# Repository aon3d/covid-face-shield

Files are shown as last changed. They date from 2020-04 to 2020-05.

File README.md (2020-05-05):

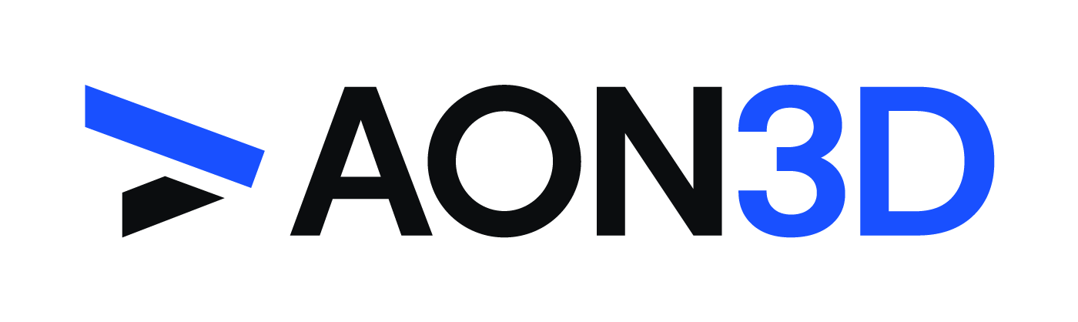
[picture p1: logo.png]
AON3D Logo (https://www.aon3d.com/)


# COVID-19 Face Shield

> [Need 3D Printed Medical Supplies to Fight COVID-19?](https://www.aon3d.com/3d-printed-medical-supplies-to-fight-covid-19/)

TL;DR: [Here is what the model looks like](models/COVID-001-Face-Shield-Frame-R01.STL).

The government of Canada has [recently come out with guidance](https://www.canada.ca/en/health-canada/services/drugs-health-products/medical-devices/covid-19-unconventional-manufacturing-personal-protective-equipment.html) regarding unconventional manufacturing of personal protective equipment in response to COVID-19.
As there are already many sites, forums, and social media efforts organizing people with access to 3D printers to support their local healthcare workers, we wanted to help standardize the design efforts.

To avoid medical professionals and our front line workers from having to adapt to a multitude of designs from different sources, we hope that grassroots efforts adopt a common design to minimize chances of a negative user experience.
As such, we are publishing our design, assembly instructions, MSDS, QC checklist, and all other documentation to help jumpstart others who want to get involved and help.

## How are we helping?

We are working with local health authorities in Montréal to produce desperately needed medical supplies and protective equipment.
Specifically, we are fabricating face shield to help protect our front line workers from splash and debris.

Our design and manufacturing methodology focuses on fulfilling short-term needs using additive manufacturing (e.g., 3D printing) to act as a stopgap while organizing medium-volume manufacturing (e.g., laser cutting, die cutting).
This two-step approach leverages our expertise (additive manufacturing) as well as a robust and local supply chain.
In this way, urgent needs due to shortages can be successfully satisfied while large-volume manufacturing (e.g., molding) catches up.
As such, the chosen face shield design is optimized for both laser cutting and 3D printing.

<p>
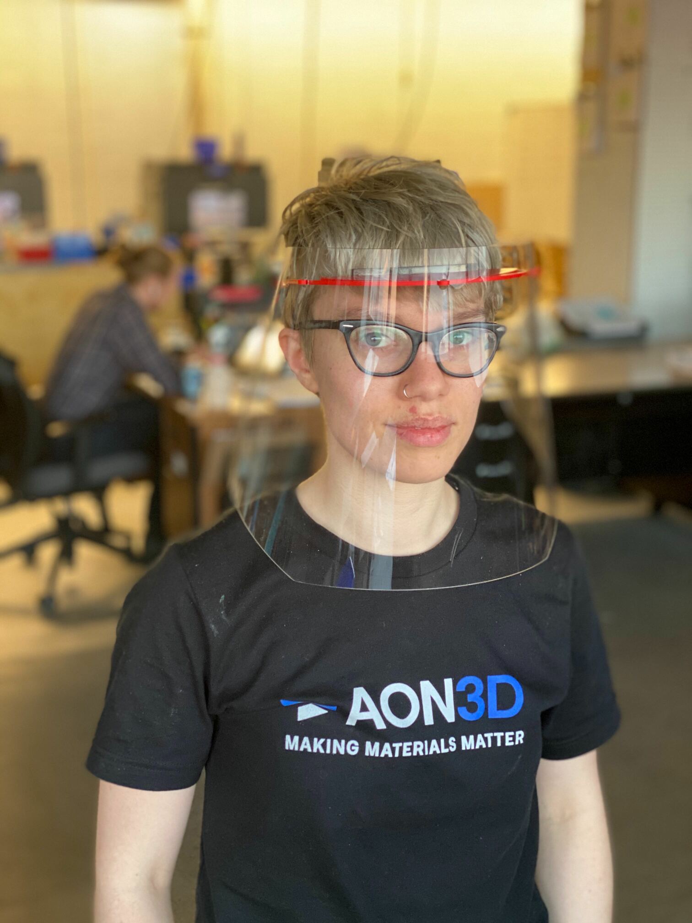
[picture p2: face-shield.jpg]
Face shield.

</p>

## Contents

- [COVID-19 Face Shield](#covid-19-face-shield)
  - [How are we helping?](#how-are-we-helping)
  - [Contents](#contents)
  - [Face Shield Design](#face-shield-design)
    - [Requirements and Specifications](#requirements-and-specifications)
      - [Visor](#visor)
      - [Frame](#frame)
    - [Bill of Materials](#bill-of-materials)
    - [Handling](#handling)
    - [Packaging](#packaging)
      - [Bag A (6” poly tubing)](#bag-a-6-poly-tubing)
      - [Bag B (12” poly tubing)](#bag-b-12-poly-tubing)
      - [Bag C (12” poly tubing)](#bag-c-12-poly-tubing)
      - [Box](#box)
  - [Design Files](#design-files)
  - [Documentation](#documentation)
  - [Printing Instructions](#printing-instructions)
    - [Printer Preparation](#printer-preparation)
    - [Frame Printing](#frame-printing)
    - [Frame Removal](#frame-removal)
  - [Development](#development)
    - [PDF Generation](#pdf-generation)
      - [Requirements](#requirements)
      - [Procedure](#procedure)
    - [Releases](#releases)
  - [Disclaimer](#disclaimer)

## Face Shield Design

Our face shield design is based on the [open-source work published by Georgia Tech](https://pwp.gatech.edu/rapid-response/face-shields/).
While the design is nearly identical, we have made the following modifications:

- Visor
  - Diameter of snap-on holes increased from 6.35mm to 7mm for an easier fit
- Frame
  - -0.25mm horizontal compensation
  - Thickness of 1/8" (3.175mm)
  - A [second iteration of the frame](models/COVID-001-Face-Shield-Frame_CNC_1_8-R01.STEP) is available and accommodates CNC milling with a 1/8" cutter

These modifications were done to better support our specialty, additive manufacturing, while also being compatible with future medium volume production methods, such as laser cutting and CNC milling.

### Requirements and Specifications

#### Visor

- Must provide adequate coverage (CSA Z94.3 Sections 10.2.1/10.2.2/10.3/10.4)
- Should made of optically clear, distortion free, lightweight materials (CSA Standard Z94.3.1-16)
- Should be free of visible defects or flaws that would impede vision (ANSI Z87.1 Section 9.4)
- Should allow adequate space between the wearer’s face and the inner surface of the visor to allow for the use of ancillary equipment (medical/surgical mask, respirator, eyewear, etc.)
- Device should withstand impact from sharp or fast projectiles (ANSI Z87.1 Section 9.2 and 9.3, CSA Z94.3 Section 10.1)
- Material: PC, PETG, PET, Acetal, POM, Polypropylene, or PVC
- Thickness: 0.01” - 0.03”

#### Frame

- Device should fit snugly to afford a good seal to the forehead area and to prevent slippage of the device
- User contacting materials should provide adequate material biocompatibility (skin sensitivity and cytotoxic testing) (ISO 10993-5, 10)
- Must resist isopropyl alcohol (IPA)
- Material: PC, ABS, or Acetal
- Thickness: 1/8" or 3/16"

### Bill of Materials

| Item | Qty | Comments |
|---|---|---|
| Frame | 1 | Laser cut or 3D printed |
| Visor | 1 | Laser or die cut |
| Elastic | 4+ | Size 33 (e.g., McMaster-Carr `12205T78`) |

### Handling

As it seems a person can carry the virus and be asymptomatic, it is best to act as if you may be contagious and take precautions to avoid contaminating the face shield during production.

- Wash your hands before entering the manufacturing area
- Wash your hands before removing prints
- Wipe down tools with IPA before using them to remove prints
- Wear a mask while handling prints
- Do not enter the manufacturing area unless you are the designated operator on shift
- Prints are immediately bagged after removal from the machine

### Packaging

To make the user experience as simple as possible for front line workers, the following packaging procedure is recommended:

#### Bag A (6” poly tubing)

- 40x elastics

#### Bag B (12” poly tubing)

- 10x frames

#### Bag C (12” poly tubing)

- 10x face shield kits
  - Bag A
  - Bag B
  - 10x visors
  - Assembly instructions

#### Box

 - MSDS
 - 10x Bag C

## Design Files

All design files may be found in the [models](models/) folder.

- `DXF` files are for laser cutting
- `STL` files are for 3D printing
- `SLDPRT` and `STEP` files are for 3D CAD software (e.g., Solidworks, Inventor, Fusion 360)
- `factory` files are for [Simplify3D](https://www.simplify3d.com/) and are designed to work for the [AON-M2 industrial 3D printer](https://www.aon3d.com/aon-m2-2020-industrial-3d-printer/)

## Documentation

All documentation files may be found in the [docs](docs/) folder.
PDFs of the documentation may be found [here](https://github.com/aon3d/covid-face-shield/releases/latest).

- Material Safety Data Sheets ([English](docs/msds-en.md), [French](docs/msds-fr.md) and [Spanish](docs/msds-es.md)) are available
- [Assembly instructions](docs/assembly.md)

## Printing Instructions

The following instructions are intended for printing using the AON-M2 or AON-M2 2020.

### Printer Preparation

1. Install a 0.6 mm nozzle heater block assembly. Instructions [here](https://docs.aon3d.com/maintenance/replace_hba/).
2. Install the aluminum build plate. Ensure that the Kapton tape is in good condition on all the surfaces. (If not, follow [this procedure](https://docs.aon3d.com/maintenance/kapton_application/) to replace it.
3. Clean the surface with IPA (isopropyl alcohol), minimum concentration of 70% for disinfection purposes.
4. Apply an adhesive to the build platform to ensure ABS adhesion. Dimafix or hairspray are tested adhesives for ABS.
4. Load ABS in the 0.6 mm toolhead you want to use. Instructions [here](https://docs.aon3d.com/operation/material_switch/).
5. Preheat the machine to the following temperatures:

| Component  | Temperature |
|:----------:|:-----------:|
| Build platform  | 105°C  |
| Chamber    | 60°C        |

6. Once the chamber has reached thermal equilibrium, initiate the probing sequence on the entire bed  and set the Z offset. Instructions [here](https://docs.aon3d.com/calibration/z_calibration/).

Use these probe bounds:

| Parameter  | Value |
|:----------:|:-----:|
| Left       | 15    |
| Right      | 435   |
| X Count    | 10    |
| Front      | 15    |
| Back/Rear  | 435   |
| Y Count    | 10    |

### Frame Printing

We have included two generated G-code files that are ready for use on the AON-M2 and AON-M2-2020.
They are intended for use with ABS and a 0.6 mm nozzle.
One G-code file is specific for printing with T0 (left toolhead) and the other is for use with T1 (right toolhead).

If you wish to modify the files, the original factory files for use with Simplify 3D have been included.
However, the specified settings have been tested and any modification may cause print defects.

Each print will yield 5 face shield frames.

Plan 112g of ABS filament and just over 2 hours of print time per print.

### Frame Removal

How to remove the part from the build platform. Proceed following the aformentioned [handling](#handling) guidelines.

**The parts and machines are hot!**
- At the end of the print, the toolheads will move to the back of the machine for easy access to the printed frames.
- The build platform and the chamber will remain heated to allow for a quick restart.
- Remove the skirt (single outline of material).
- With the scraper, carefully detach the extremity of the face shield frame. This will initiate the rest of the removal. Gently detach the part by placing the scraper under the part.
- Place the parts in a sanitized bag for storage.

## Development

### PDF Generation

#### Requirements

- [`pandoc`](https://pandoc.org/)
- `make`
- [`ghostscript`](https://www.ghostscript.com/)
- `texlive`

#### Procedure

To generate all PDFs:

```bash
make pdf
```

### Releases

- This repo uses [Calendar Versioning (`CalVer`)](https://calver.org/overview.html), with the following format: `YYYY.MM.DD`
- Generated PDFs should be attached to the [GitHub release](https://github.com/aon3d/covid-face-shield/releases/latest)

## Disclaimer

Please see [`DISCLAIMER.md`](DISCLAIMER.md).

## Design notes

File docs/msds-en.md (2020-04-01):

---
title: Material Safety Data Sheet
logo: logo.png
titlepage: true
---

# Identification

| | |
|---|---|
| Product Name | Face Shield |
| Product Code | COVID-FACE-SHIELD |
| Use(s) | Face protection from splash and other debris |
| Company Name | Made in 3D Canada Inc. (dba AON3D) |
| Telephone | \+1 833-772-6633 |

# Hazard Identification

| | |
|---|---|
| Potential Hazard | Combustible |
| Other Comments | N/A |

# Composition/Information on Ingredients

| Component | Material(s) |
|---|---|
| Frame | ABS, HIPS, or Acrylic |
| Visor | Polycarbonate, PETG, PET, Acetal, PVC, or Polypropylene |
| Strap | Polyester, Rubber, Polypropylene, and/or Nylon |
| Buckle | Plastic |

# First-aid Measures

| | |
|---|---|
| Inhalation (breathing) | In case of inhalation of smoke or burnt, consult physician. |

# Fire-fighting Measures

| | |
|---|---|
| Flashpoint | N/A |
| Flammable class | Burnable |
| Extinguishing media | Class A fire extinguisher |
| General hazard | Evacuate personal downwind of fire to avoid inhalation of irritation or harmful fumes and smoke. |
| Hazardous combustion products | Harmful gases |

# Accidental Release Measures

Collect and treat according to local plastics waste procedures.

# Handling and Storage

| | |
|---|---|
| Handling & Storage | Keep away from flammable substances and ignition sources, and store in cool and dry condition. |

# Exposure Controls/Personal Protection

| | |
|---|---|
| Breath protection | Not required |
| Skin protection | Not required |
| Ventilation | Not required |

# Physical and Chemical Properties

| | |
|---|---|
| Appearance | Colour varies |

# Stability and Reactivity

| | |
|---|---|
| Chemical Stability | Stable under normal room conditions of temperature and pressure. |
| Incompatible products | None |
| Hazardous decomposition product | N/A |

# Toxicological Information

| | |
|---|---|
| Toxicity | The product is non-toxic. |
| Eye/skin/sensitization effect | This product is not expected to cause significant irritation. |

# Ecological Information

Not biodegradable.

# Disposal Considerations

Treat according to the local plastics waste procedures.

# Transport Information

Not regulated or restricted.

# Regulatory Information

## Minimum Specifications in Urgent Manufacturing Scenarios

- Device must provide adequate coverage (CSA Z94.3 Sections 10.2.1/10.2.2/10.3/10.4).
- Device should made of optically clear, distortion free, lightweight materials (CSA Standard Z94.3.1-16)
- Device should be free of visible defects or flaws that would impede vision (ANSI Z87.1 Section 9.4)
- The device should allow adequate space between the wearer’s face and the inner surface of the visor to allow for the use of ancillary equipment (medical/surgical mask, respirator, eyewear, etc.)
- Device should fit snugly to afford a good seal to the forehead area and to prevent slippage of the device
- Device should withstand impact from sharp or fast projectiles (ANSI Z87.1 Section 9.2 and 9.3, CSA Z94.3 Section 10.1)
- If available, device should display anti-fog behavior on inside and outside of shield. (CSA Standard Z94.3.1-16)
- User contacting materials should provide adequate material biocompatibility (skin sensitivity and cytotoxic testing) (ISO 10993-5, 10)

# Other Information

The information furnished herein is believed to be accurate and
represents the best data currently available to us. No warranty,
expressed or implied, is made and AON3D assumes no legal responsibility
or liability resulting from its use. Use product for intended purpose
only.

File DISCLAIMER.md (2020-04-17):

# Disclaimer

While MADE IN 3D CANADA INC (DBA AON3D) (“Supplier”) endeavours to provide information that is correct, Supplier disclaims all warranties, representations and conditions of any kind with respect to the published files online which can be used to 3D print face shield frames ( “Files” ) whether express, implied or collateral or whether arising by statute, course of dealing, custom or usage of trade, including, without limitation: (i) that  Files  are fit for a particular purpose, (ii) that the  Files  are accurate or  complete, (iii) that defects or errors in the Files (be they human or computer error(s)) will be corrected, and (iv) that the  Files  are free from viruses or harmful components.
You acknowledge and agree that the Files have been provided without any of the certifications required by law or regulation from any governmental body including, without limitation, Health Canada as MEDICAL FACE SHIELDS ARE REGULATED CLASS I MEDICAL DEVICES.
You expressly agree that your use of or inability to use the Files is entirely at your own risk.

SUBJECT TO APPLICABLE LAW, IN NO EVENT SHALL SUPPLIER OR ITS AFFILIATE AND THEIR RESPECTIVE OFFICERS, DIRECTORS, EMPLOYEES, AGENTS, REPRESENTATIVES, CONTRACTORS OR LICENSORS BE LIABLE FOR DAMAGES OF ANY KIND, INCLUDING, WITHOUT LIMITATION, ANY DIRECT, SPECIAL, INDIRECT, INCIDENTAL OR CONSEQUENTIAL DAMAGES INCLUDING, WITHOUT LIMITATION, ANY LOSS OR DAMAGES IN THE NATURE OF, OR RELATING TO, LOST REVENUE, LOST PROFIT, BUSINESS INTERRUPTION, INACCURATE INFORMATION, LOST PROGRAMS OR DATA OR ANY OTHER LOSS INCURRED IN CONNECTION WITH YOUR USE, INABILITY TO USE, OR MISUSE OF THE FILES, REGARDLESS OF THE CAUSE AND WHETHER ARISING IN CONTRACT (INCLUDING FUNDAMENTAL BREACH, TORT (INCLUDING NEGLIGENCE), OR ANY OTHER BASIS OR OTHERWISE.
THE FOREGOING LIMITATION SHALL APPLY EVEN IF SUPPLIER KNEW OF OR OUGHT TO HAVE KNOWN OF THE POSSIBILITY OF SUCH DAMAGES.

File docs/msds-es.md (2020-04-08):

---
title: Hoja de seguridad de materiales
logo: logo.png
titlepage: true
---

# Identificación

| | |
|---|---|
| Nombre del Producto | Escudo Facial |
| Código del Producto | COVID-FACE-SHIELD |
| Uso(s) | Proteción facial contra salpicaduras y otras partículas |
| Nombre de la compañia | Hecho por 3D Canada Inc. (dba AON3D) |
| Teléfono | \+1 833-772-6633 |

# Identificación de peligros

| | |
|---|---|
| Peligro potencial | Combustible |
| Otros comentarios | N/A |

# Composición/Información de los componentes

| Componente | Material(es) |
|---|---|
| Marco | ABS, HIPS, or Acrílico |
| Visor | Policarbonato, PETG, PET, Acetato, PVC, or Polipropileno |
| Correa | Poliester, Caucho, Polipropileno, y/o Nylon |
| Hebilla | Plástico |

# Primeros auxilios

| | |
|---|---|
| Inhalación (respiracion) | En caso de inhalación humo o incendio, consulte a su médico. |

# Medidas a tomar en caso de incendio

| | |
|---|---|
| Punto de ruptura | N/A |
| Tipo de combustible | Combustible |
| Forma de extinción | Extintor Tipo A |
| Peligro general | Evacue al personal en contra del viento, para evitar su inhalación y para evitar gases o humo irritante. |
| Productos combustibles peligros | Gases peligrosos |

# Medidas en caso de derrames accidentales

Recoletar y tratar de acuerdo a los procedimientos locales de disposición de plásticos.

# Manipulación y almacenamiento

| | |
|---|---|
| Manipulacion y almacenamiento | Mantener alejado de substancias inflamables o de fuentes de combustión, almacenar en un lugar fresco y seco. |

# Controles de Exposición /Protección personal

| | |
|---|---|
| Protección de respiración | No es requerida |
| Protección de piel | No es requerida |
| Ventilación | Not required |

# Propiedades físicas y Químicas

| | |
|---|---|
| Apariencia | El color varía |

# Estabilidad y reactividad

| | |
|---|---|
| Estabilidad química | Estable bajo condiciones normales de ambiente, temperatura y presión. |
| Productos incompatibles | None |
| Descomposición peligrosa de materiales | N/A |

# Información toxicológica

| | |
|---|---|
| Toxicidad | El producto no es tóxico. |
| Efecto en los ojos/piel/sensibilización | No se espera que este producto cause irritación significativa. |

# Información ecológica

No es biodegradable

# Consideraciones para depósitar a la basura

Trate de acuerdo a los procedimientos locales de manejo de plásticos.

# Información de trasporte

No regulado o restringido

# Información regulatoria

## Especificaciones mínimas en escenarios urgentes de manofactura

- El dispositivo debe suministrar suficiente cobertura (CSA Z94.3 Sections 10.2.1/10.2.2/10.3/10.4).
- El dispositivo debe estas hecho de materiales trasparentes libres de distorsion y de materiales livianos (CSA Standard Z94.3.1-16)
- El dispositivo debe estar libre de defectos visibles o fallas que impidan la visión (ANSI Z87.1 Section 9.4)
- El dispositivo debe permitir un espacio adecuado entre la cara de quien lo porta y la superficie interna del visor. de esta forma permitiendo el uso de equipo complementario (medico/tapabocas, respiradores, gafas, etc.)
- El dispositivo debe quedar los suficientemente comodo para permitir un buen sellado en el area de la frente para evitar su caida.
- El dispositivo debe resistir el impacto de objetos contundentes o punzantes (ANSI Z87.1 Section 9.2 and 9.3, CSA Z94.3 Section 10.1)
- Si esta disponible, el dispositivo debe tener propiedades antiempañantes adentro o fuera del visor. (CSA Standard Z94.3.1-16)
- El usuario que tiene contacto con los materiales  deben ofrecer aceduada bio-compatibilidad  (Sensibilidad a la piel y estudios citotóxico) (ISO 10993-5, 10)

# Otra información

La información contenida se cree que es precisa
y representa la información que esta disponible para nosotros . No hay garantía,
expresa o implicita. AON3D no asume ninguna responsabilidad legal
o contractual que resulte de su uso. Use el producto para su propósito indicado.

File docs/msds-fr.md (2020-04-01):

---
title: Fiches de données de sécurité
logo: logo.png
titlepage: true
---

# Identification

| | |
|---|---|
| Nom du produit | Écran facial |
| Code produit | COVID-FACE-SHIELD |
| Utilisation | Protection du visage contre les éclaboussures et autres débris |
| Nom de la compagnie | Made in 3D Canada Inc. (dba AON3D) |
| Téléphone | \+1 833-772-6633 |

# Identification des dangers

| | |
|---|---|
| Danger potentiel | Combustible |
| Autres commentaires | ND |

# Composition/information sur les composants

| Composant | Matériaux |
|---|---|
| Cadre | ABS, HIPS ou acrylique |
| Visière | Polycarbonate, PETG, PET, acétal, PVC ou polypropylène |
| Sangle | Polyester, caoutchouc, polypropylène et / ou nylon |
| Boucle | Plastique |

# Premiers soins

| | |
|---|---|
| Inhalation (respiration) | En cas d'inhalation de fumée ou de brûlure, consulter un médecin. |

# Mesures à prendre en cas d'incendie

| | |
|---|---|
| Point de rupture | ND |
| Classe inflammable | Brûlable |
| Moyens d'extinction | Extincteur de classe A |
| Risque général | Évacuer le feu personnel sous le vent pour éviter l'inhalation d'irritations ou de fumées et de fumée nocives. |
| Produits de combustion dangereux | Gaz nocifs |

# Mesures à prendre en cas de déversements accidentels

Collecter et traiter conformément aux procédures locales de gestion des
déchets plastiques.

# Manutention et stockage

| | |
|---|---|
| Manipulation et stockage | Conserver à l'écart de substances inflammables et sources d'ignition, et stocker dans un endroit frais et l'état sec. |

# Contrôles de l'exposition/protection individuelle

| | |
|---|---|
| Protection respiratoire | Non requis |
| Protection de la peau | Non requis |
| Ventilation | Non requis |

# Propriétés physiques et chimiques

| | |
|---|---|
| Apparence | La couleur varie |

# Stabilité et réactivité

| | |
|---|---|
| Stabilité chimique | Stable dans des conditions ambiantes normales de température et de pression. |
| Produits incompatibles | Aucun |
| Produit de décomposition dangereux | ND |

# Données toxicologiques

| | |
|---|---|
| Toxicité | Le produit n'est pas toxique. |
| Effet yeux/peau/sensibilisation | Ce produit ne devrait pas causer d'irritation importante. |

# Données écologiques

Non biodégradable.

# Données sur l'élimination du produit

Traiter conformément aux procédures locales de traitement des déchets
plastiques.

# Informations relatives au transport

Non réglementé ou limité.

# Informations sur la réglementation

## Spécifications minimales dans les scénarios de fabrication urgents

- L'appareil doit fournir une couverture adéquate (CSA Z94.3 Sections 10.2.1 / 10.2.2 / 10.3 / 10.4).
- Le dispositif doit être fait de matériaux légers, optiquement transparents, sans distorsion (se référer à la norme CSA Z94.3.1-16 et Note de bas de page 1)
- L'appareil doit être exempt de défauts visibles ou de défauts qui pourraient gêner la vision (ANSI Z87.1 Section 9.4)
- L’appareil doit laisser un espace suffisant entre le visage du porteur et la surface intérieure de la visière pour permettre l’utilisation d’équipements auxiliaires (masque médical / chirurgical, respirateur, lunettes, etc.) Note de bas de page 1.
- L'appareil doit être bien ajusté pour assurer une bonne étanchéité à la zone du front et pour empêcher le glissement de l'appareil Note de bas de page 1.
- L'appareil doit résister à l'impact de projectiles pointus ou rapides (ANSI Z87.1 sections 9.2 et 9.3, CSA Z94.3 section 10.1)
- Si disponible, l'appareil doit afficher un comportement anti-buée à l'intérieur et à l'extérieur du bouclier. (Norme CSA Z94.3.1-16)
- Les matériaux en contact avec l'utilisateur doivent fournir une biocompatibilité adéquate des matériaux (sensibilité cutanée et tests cytotoxiques) (ISO 10993-5, 10)

# Autres informations

Les informations fournies ici sont considérées comme exactes et
représentent les meilleures données actuellement disponibles pour nous.
Aucune garantie, expresse ou implicite, n'est faite et AON3D n'assume
aucune responsabilité légale ou obligation résultant de son utilisation.
N'utilisez le produit qu'aux fins prévues.

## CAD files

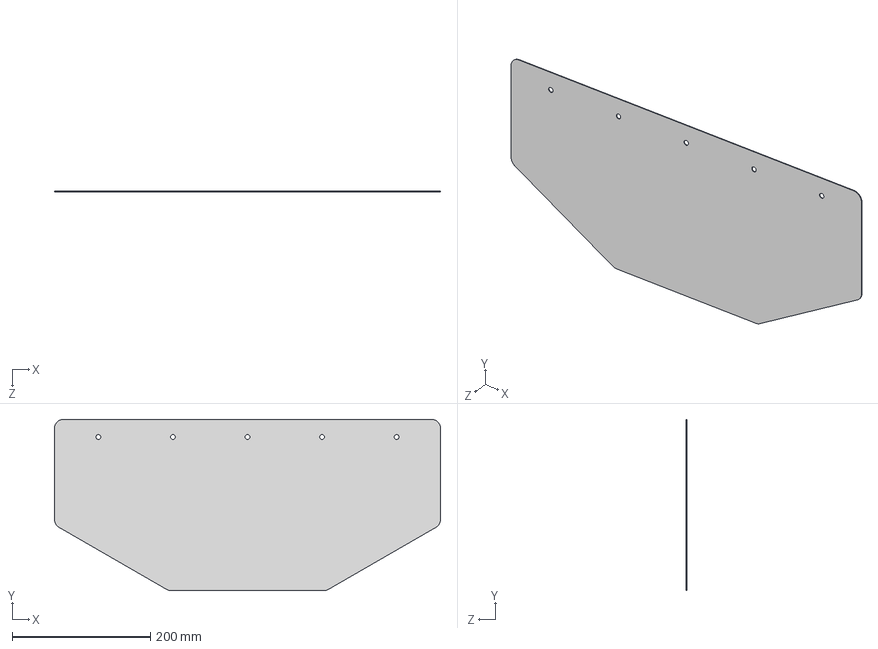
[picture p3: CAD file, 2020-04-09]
models/COVID-002-Visor-7mm-holes-R01.STEP
558.8 x 247.6 x 1.02 mm

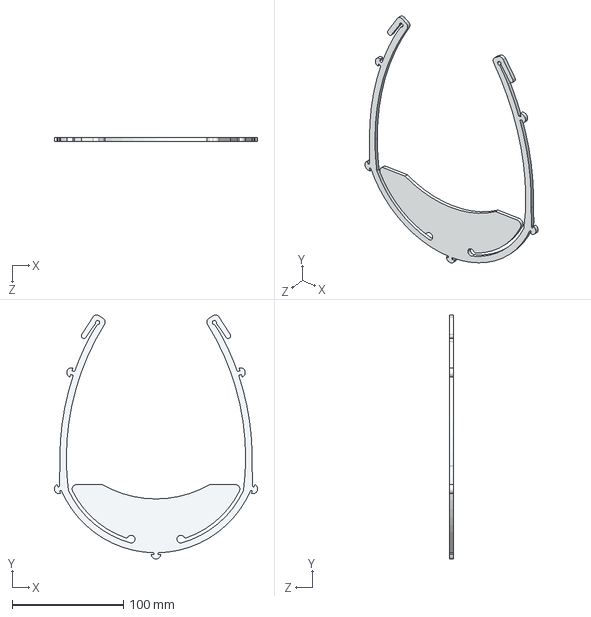
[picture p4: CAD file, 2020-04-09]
models/COVID-001-Face-Shield-Frame-R01.STEP
182.4 x 218.9 x 3.17 mm

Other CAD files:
models/COVID-001-Face-Shield-Frame-R01.DXF
models/COVID-001-Face-Shield-Frame-R01.STL
models/COVID-001-Face-Shield-Frame-R01.sldprt
models/COVID-002-Visor-7mm-holes-R01.DXF
models/COVID-002-Visor-7mm-holes-R01.sldprt

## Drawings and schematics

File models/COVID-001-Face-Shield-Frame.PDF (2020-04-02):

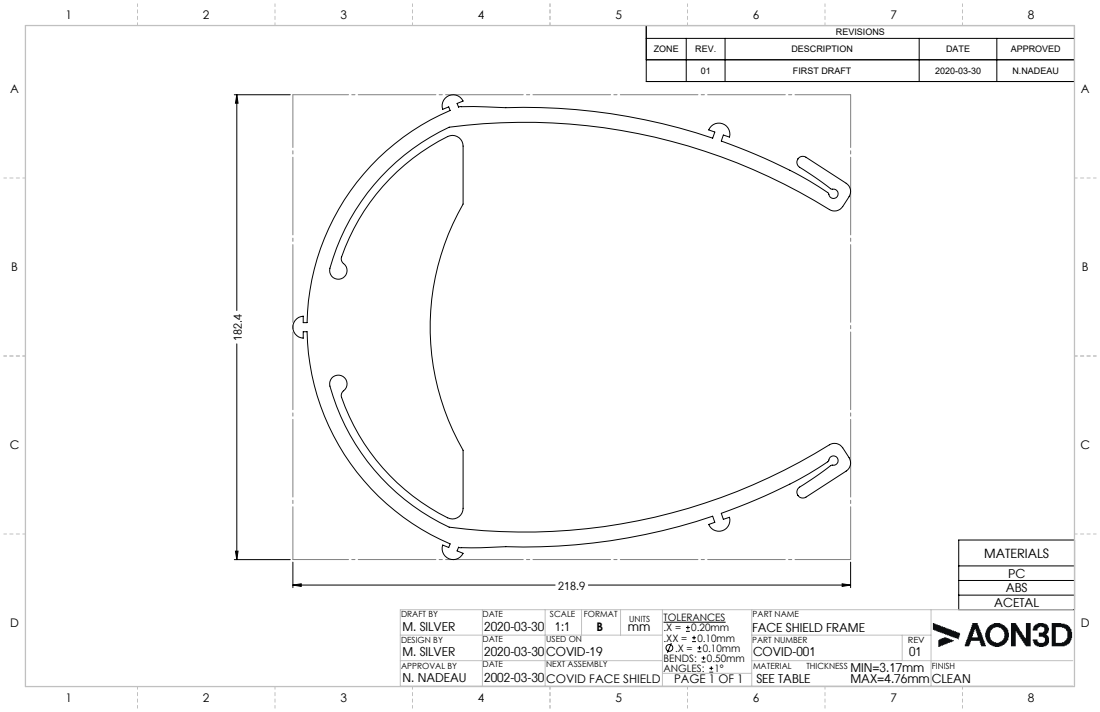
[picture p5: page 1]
PART NUMBER; REV; SEE TABLE; DRAFT BY; DESIGN BY; APPROVAL BY; M. SILVER; N. NADEAU; SCALE; PART NAME; USED ON; FACE SHIELD FRAME; NEXT ASSEMBLY COVID FACE SHIELD; THICKNESS MIN=3.17mm

REVISIONS

ZONE | REV. | DESCRIPTION | DATE | APPROVED

01 | FIRST DRAFT | 2020-03-30 | N.NADEAU

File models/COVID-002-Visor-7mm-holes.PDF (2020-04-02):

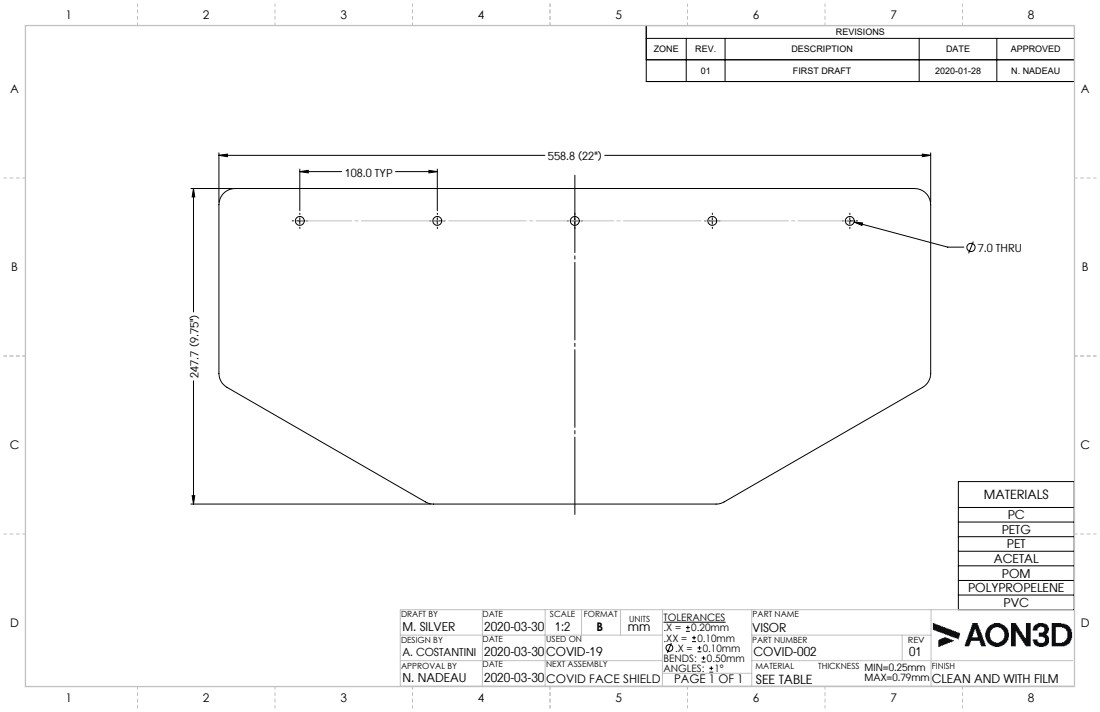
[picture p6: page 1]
108.0 TYP; 7.0 THRU; PART NUMBER; REV; SEE TABLE; DRAFT BY; DESIGN BY; APPROVAL BY; A. COSTANTINI; M. SILVER; N. NADEAU; SCALE; PART NAME; USED ON; CLEAN AND WITH FILM; NEXT ASSEMBLY COVID FACE SHIELD; THICKNESS MIN=0.25mm

REVISIONS

ZONE | REV. | DESCRIPTION | DATE | APPROVED

01 | FIRST DRAFT | 2020-01-28 | N. NADEAU

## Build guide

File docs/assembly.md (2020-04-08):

---
title: |
    Face Shield Assembly Instructions
    Instructions d'assemblage du masque facial
    Instrucciones de ensamble de mascara facial
logo: logo.png
titlepage: true
---

# Attach the visor to the frame / Fixez la visière au cadre / Fije el visor al marco



# Attach the elastic to the frame / Fixez l'élastique au cadre / Fije el elástico al marco

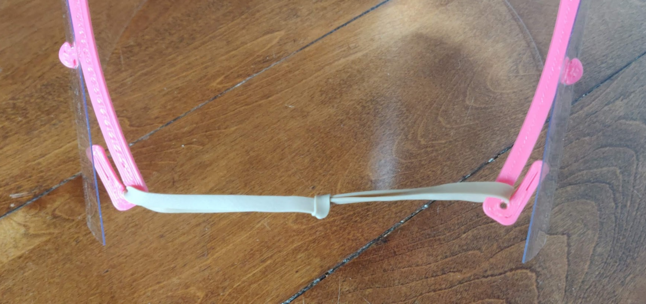
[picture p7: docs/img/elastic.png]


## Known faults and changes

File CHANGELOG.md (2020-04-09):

# Changelog

All notable changes to this project will be documented in this file.

The format is based on [Keep a Changelog](https://keepachangelog.com/en/1.0.0/),
and this project adheres to [Calendar Versioning](https://calver.org/).

## Unreleased

### Added

- `COVID-001-Face-Shield-Frame_CNC_1_8-R01` STEP and DXF for CNC milling w/ 1/8" cutter

### Changed

- Revision numbers on all model files
- Added descriptor of CNC file addition to `README.md`

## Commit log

2020-04-01 added assembly instructions
2020-04-01 assembly images
2020-04-01 added model files
    [COVID-001-Face-Shield-Frame.DXF, COVID-001-Face-Shield-Frame.STEP, COVID-001-Face-Shield-Frame.STL, COVID-001-Face-Shield-Frame.sldprt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]
2020-04-03 changed image of elastic mounting (#18)
2020-04-09 Visor STEP + 1/8" CNC Mod + Revision # + date fix (#19)
    * Add files via upload
    * Names-updated-1_8-CNC-mod-step-visor
    -Names updated with revision #
    -Mod of shield mount for CNC cutting 1/8" EM
    -Added .STEP for visor
    * Added CNC files and updated readme and changelog
    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
    [COVID-001-Face-Shield-Frame-R01.DXF, COVID-001-Face-Shield-Frame-R01.STEP, COVID-001-Face-Shield-Frame-R01.STL, COVID-001-Face-Shield-Frame-R01.sldprt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]
2020-04-13 Update print instructions in README.md (#12)
    * Update README.md
    Added printing instructions paragraph related to the M2 machine.
    * Update README.md
    * Update README.md
    * Update README.md
    * Update README.md
    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
